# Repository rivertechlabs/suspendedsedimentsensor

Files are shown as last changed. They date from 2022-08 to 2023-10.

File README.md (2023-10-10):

# :ocean:Ötz-T: suspended sediment sensor

## A note on versions:

**This sensor is prototype 3.0 (or "version Ötz-T"). The previous prototype 2.0 (or "first version") is found in this [repo](https://github.com/rivertechlabs/turbiditysensor) (new repo because I consider the two versions different enough).**

## News!

**This sensor was published in HardwareX! Read [Ötz-T: 3D-printed open-source turbidity sensor with Arduino shield for suspended sediment monitoring](https://linkinghub.elsevier.com/retrieve/pii/S2468067223000020).**

-----------------------------------------

**Improvements on this version:**
- :sleeping: Low-power [Arduino MRK WAN 1310](https://store-usa.arduino.cc/products/arduino-mkr-wan-1310) microcontroller
- :stuck_out_tongue_winking_eye: Entirely 3D printed design, so no need to beg a technician for help
- :racehorse: Longer battery life
- :dash: Turbidity, temperature and pressure sensor
- :recycle: Programmed with Arduino IDE
- :dancers: Custom printed circuit board (PCB) as an Arduino shield for an easier and cleaner assembly with a more durable design 

-----------------------------------------
A 3D-printed, open-source suspended sediment sensor for river network monitoring.
## Introduction
This repo is dedicated to the open-source turbidity sensor. More info can be found here:
- https://rivertechlabs.org/
- https://hyd.ifu.ethz.ch/research/riparian/susp-sed-sense.html

This repo contains several items to build the current prototype of the open-source turbidity sensor including:
- The code needed to upload to the microcontroller
- 3D printing files
- PCB files
- CAD files

## Code
There are two codes in the Code folder: main.ino and set_time.ino. Please follow the instructions in set time.ino about changing the date in the program. After the program has flashed, every time the Arduino restarts (disconnect and reconnect to power) it will restart the RTC time to the original compile time of the set time.ino program. To mitigate this issue, the next program, main.ino, can be immediately flashed without disconnecting power or set time.ino can be re-flashed after commenting-out line 79 (“setPCF85263();”). Follow by flashing main.ino onto the Arduino. Please note that additional libraries may need to be downloaded and added to your library (e.g. the [MS5803-05 external library](https://github.com/millerlp/MS5803_05)). The main.ino program was written to take a measurement every hour (one measurement is an average of 15 measurements) to conserve battery, but this can be changed in the code if you require higher temporal resolution to capture larger variability e.g. from flushing of sediment from a dam.

## 3D printing files
Here you will find the printer files (.gcode) and the PrusaSlicer files (.3mf). The CAD files were exported as .stp and imported into the PrusaSlicer program (free). See the .3mf files to understand the settings we used in PrusaSlicer for optimal printing. The main settings were:
- Avoid crossing perimeters [enabled]: so that there was less material to clean after printing
- 5 perimeters, 5 bottom solid layers, and AT LEAST 0.15mm layer height for all components (on the thread and cap to ensure they were waterproof, see this [article](https://blog.prusa3d.com/watertight-3d-printing-pt1-vases-cups-and-other-open-models_48949/))
- The lens inserts ("zapfen") have an even smaller layer height
- The "teeth" have variable layer height (ranging from 0.07-0.15mm to ensure that the zapfen fit into the teeth)

The .3mf files were exported as .gcode files and then printed on a Prusa I3 Mk3 and/or Mk3S Filament Printer.

## PCB
We have provided the Gerber files to directly order the PCBs. Alternatively, the .PcbDoc and .SchDoc files can be opened in Altium (the eductional license can be obtained for free) where you can export your own Gerber files. Finally, the schematic and PCB files were also provided as KiCad files so that they can be viewed and edited without Altium.

## CAD
In this folder we have the original CAD files (as STEP) so that they can be downloaded and adjusted for your project.

## Contact
For questions, please email me at droujko@ifu.baug.ethz.ch or @rivertechjess on Twitter :bird:

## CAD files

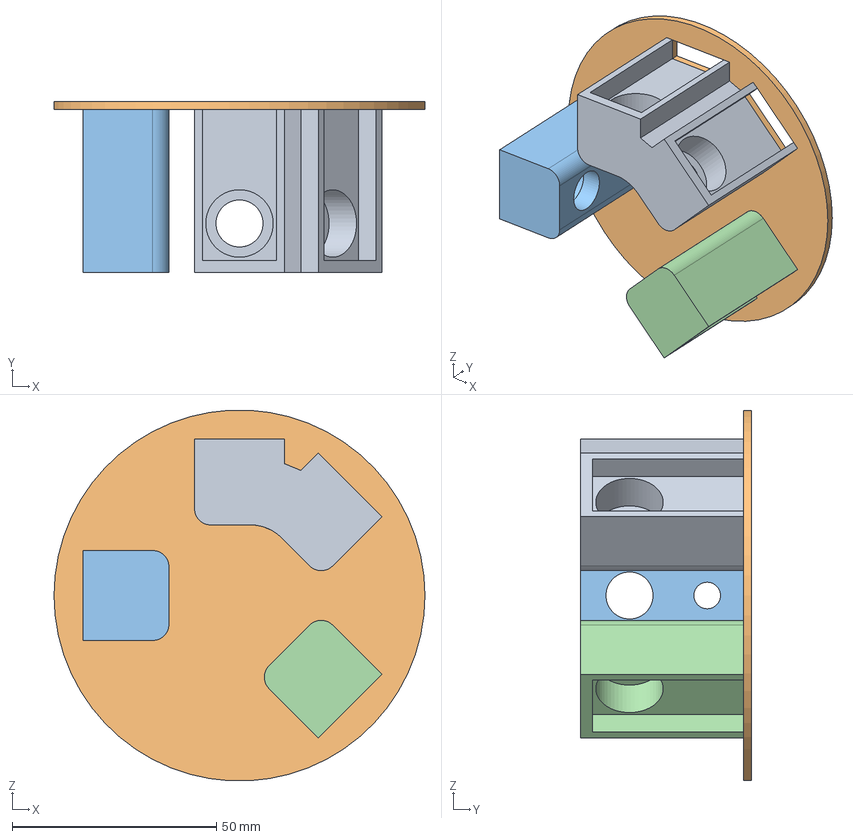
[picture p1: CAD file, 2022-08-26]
CAD/Teeth.step
90.8 x 41.8 x 90.6 mm
Legsandbody (2)
Legsandbody (3)
Legsandbody (1)

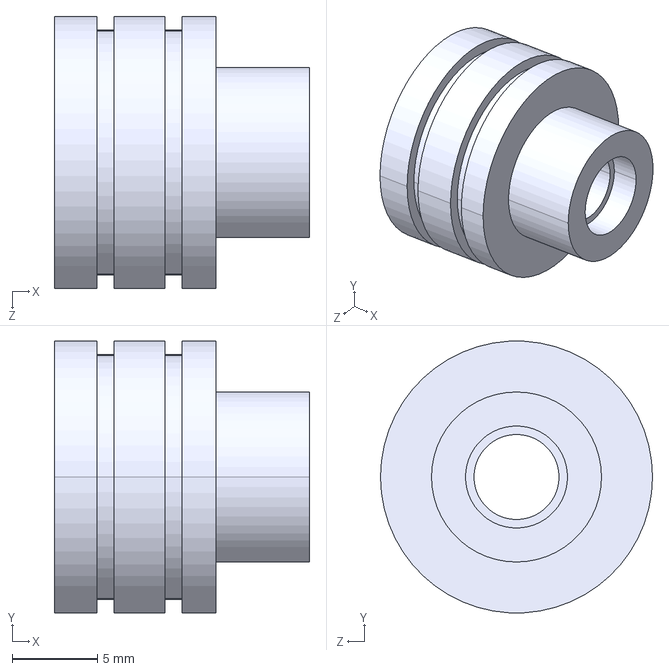
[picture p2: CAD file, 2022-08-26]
CAD/Detector_Zapfen.STEP
15.0 x 16.0 x 16.0 mm

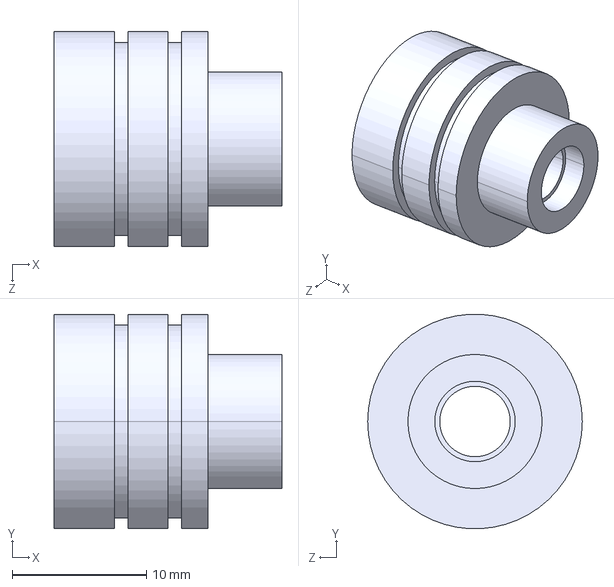
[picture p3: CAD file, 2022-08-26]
CAD/LED_Zapfen.STEP
17.0 x 16.0 x 16.0 mm

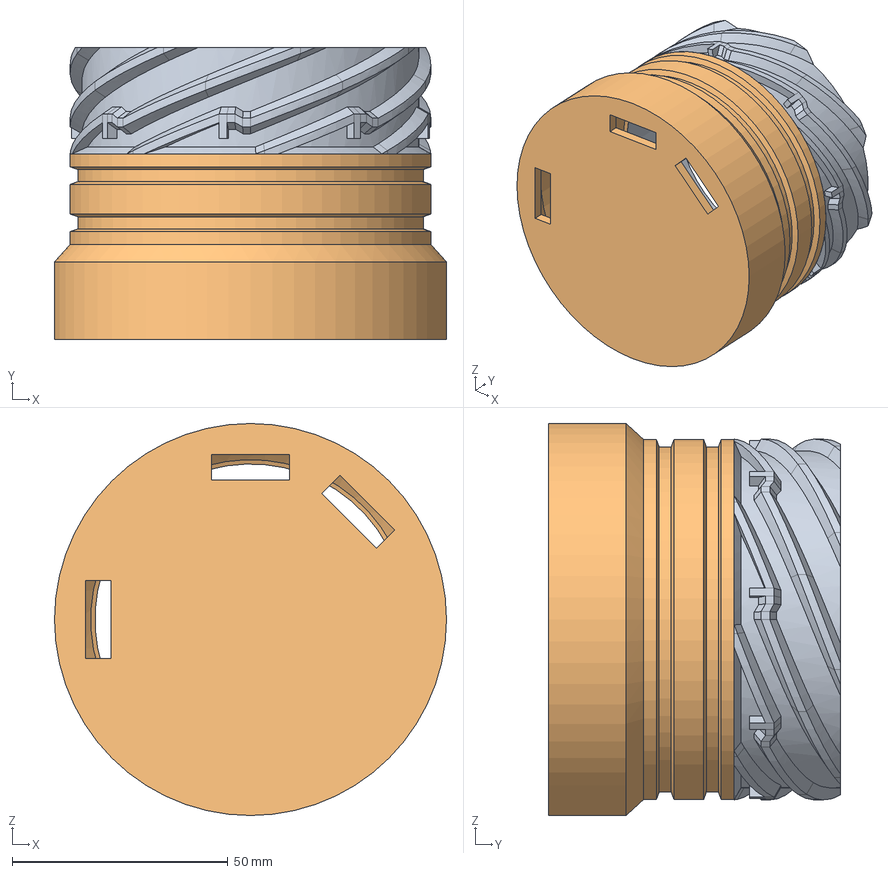
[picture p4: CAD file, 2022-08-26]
CAD/Thread.step
90.8 x 67.6 x 90.8 mm

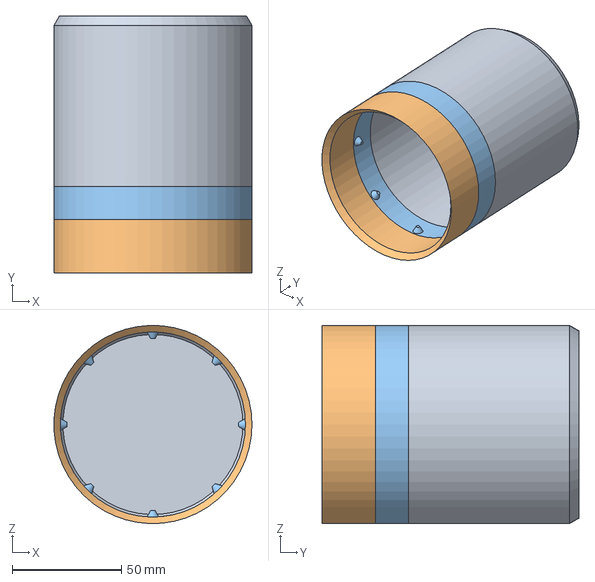
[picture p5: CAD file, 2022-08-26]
CAD/Cap.step
90.7 x 117.5 x 90.7 mm
Cap (1) (1)
Cap

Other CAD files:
3D-printing/Cap.3mf
3D-printing/Cap.stl
3D-printing/Detector_Zapfen.3mf
3D-printing/Detector_Zapfen.STL
3D-printing/LED_Zapfen.3mf
3D-printing/LED_Zapfen.STL
3D-printing/Teeth.3mf
3D-printing/Teeth.stl
3D-printing/Thread.3mf
3D-printing/Thread.stl

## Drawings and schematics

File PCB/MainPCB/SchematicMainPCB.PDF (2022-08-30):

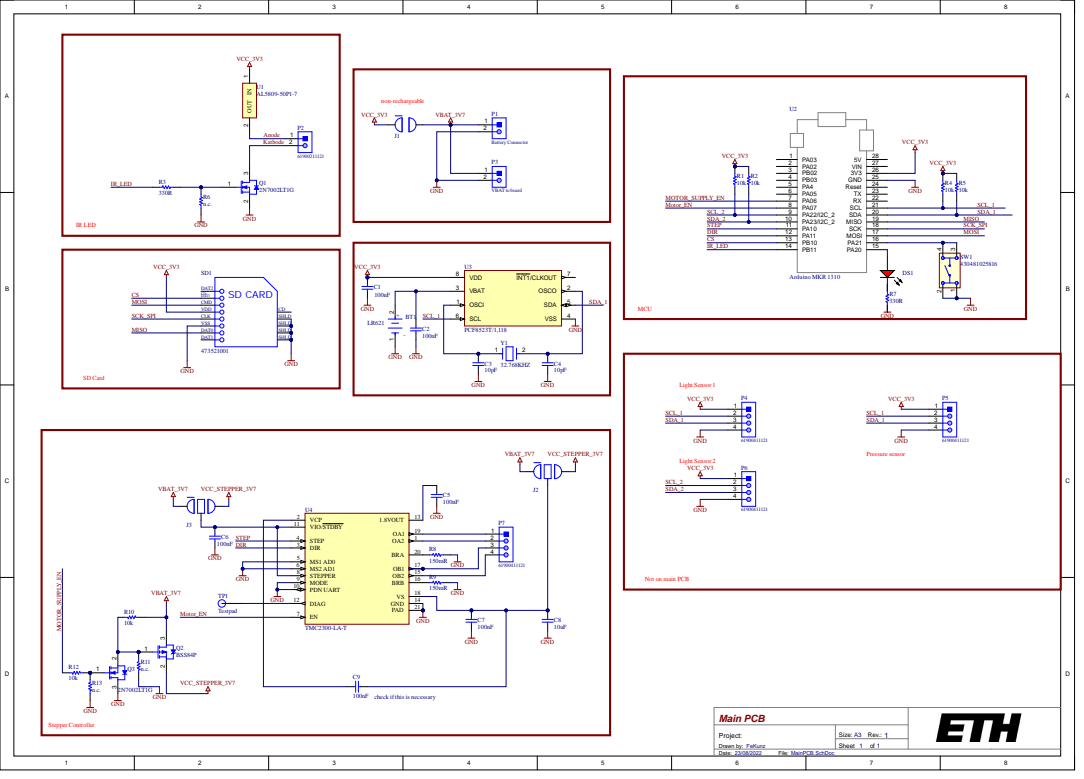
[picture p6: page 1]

1 1 | VCP VIO /ST D B Y ST E P DIR MS1 A D 0 MS2 A D 1 ST EPPE R MO D E PD N U A RT DIA G E N

Main PCB

Pro j e ct : Dra w n by: F eKu n z | Siz e : A3 Rev . : 1

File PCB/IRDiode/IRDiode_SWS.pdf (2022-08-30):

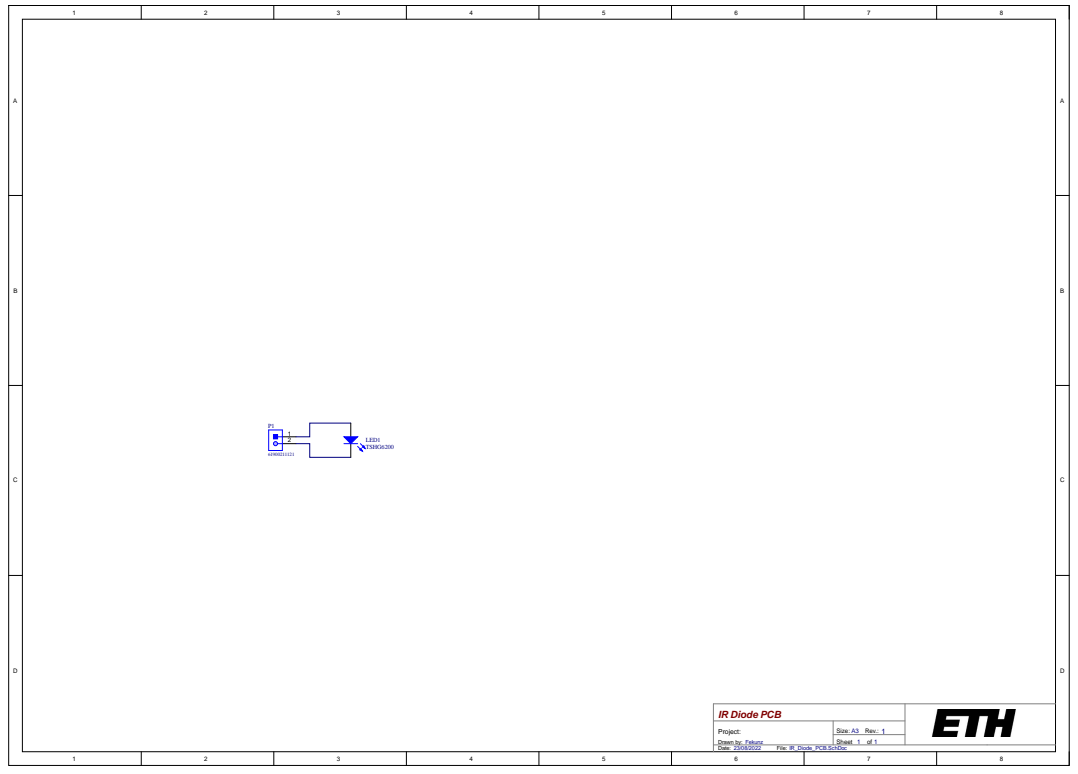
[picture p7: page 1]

IR Dio de PCB

P r oject: Drawn by: Fekun z | S ize: A 3 Rev . : 1

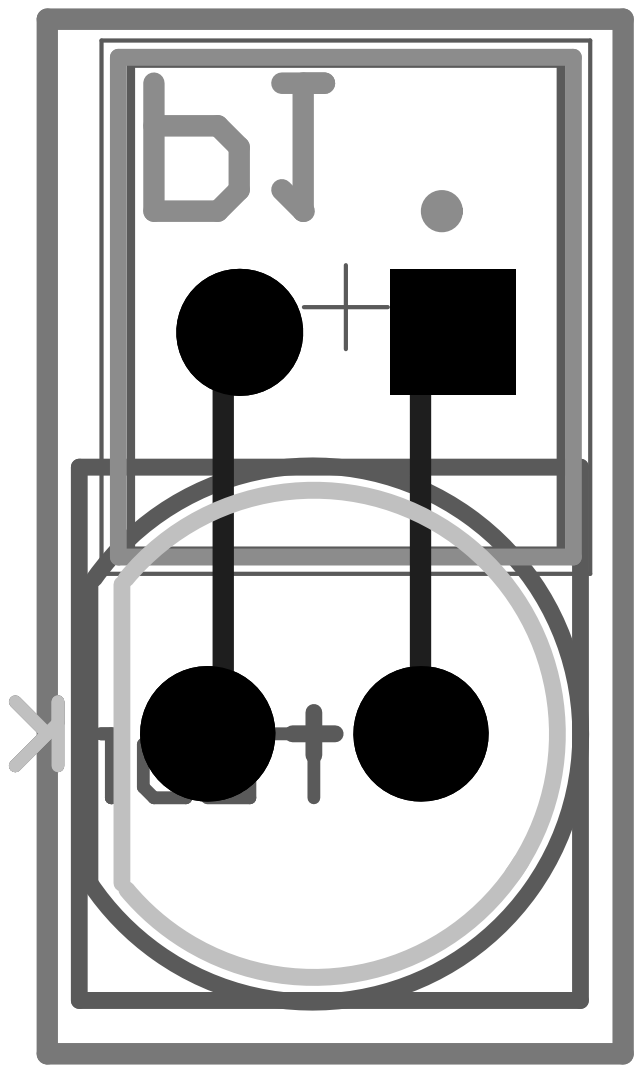
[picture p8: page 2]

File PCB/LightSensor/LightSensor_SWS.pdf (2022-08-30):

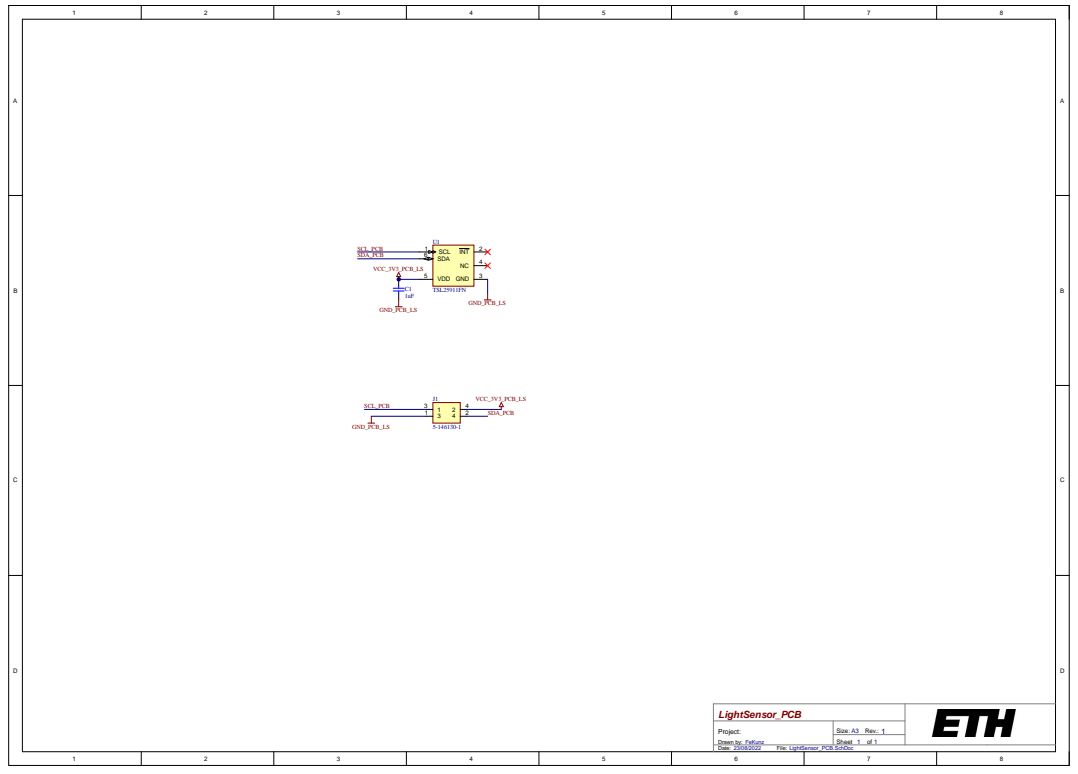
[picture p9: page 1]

LightSensor_PCB

Project: Drawn by: FeKunz | Size: A3 Rev.: 1

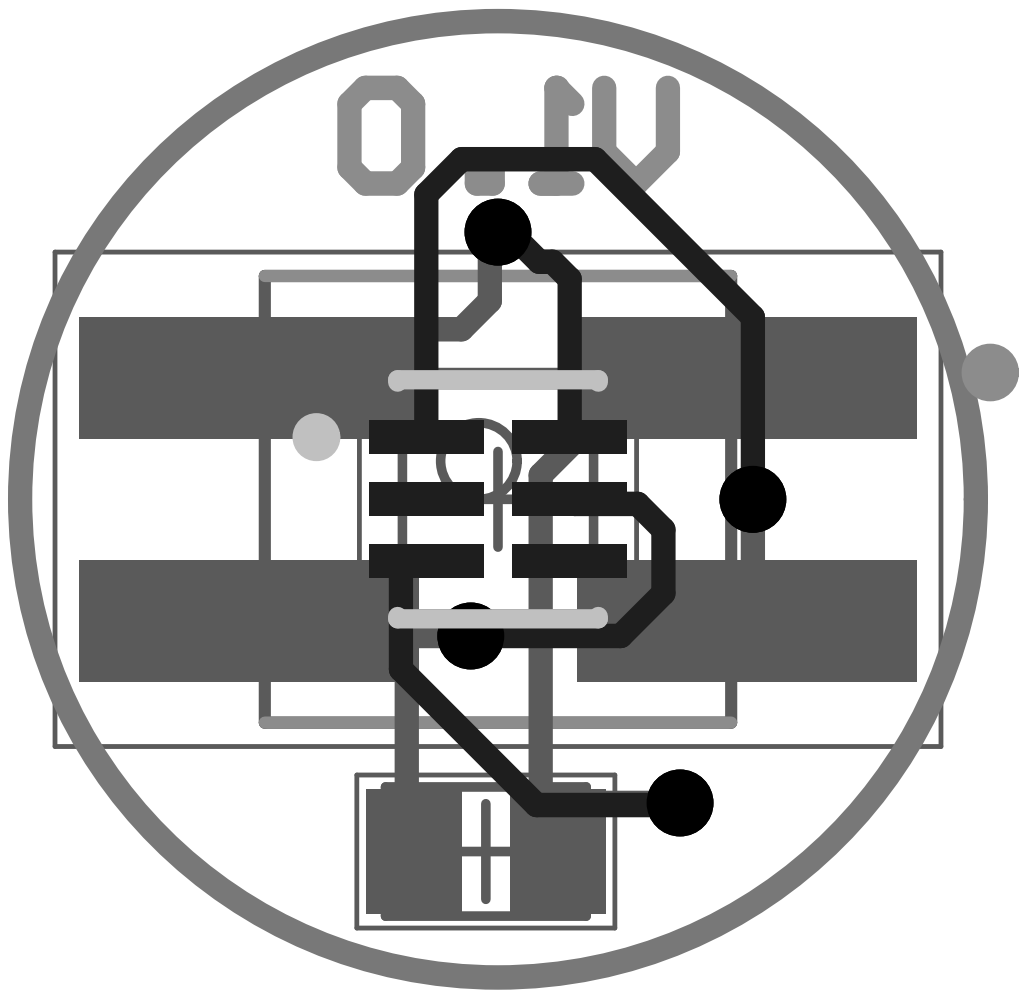
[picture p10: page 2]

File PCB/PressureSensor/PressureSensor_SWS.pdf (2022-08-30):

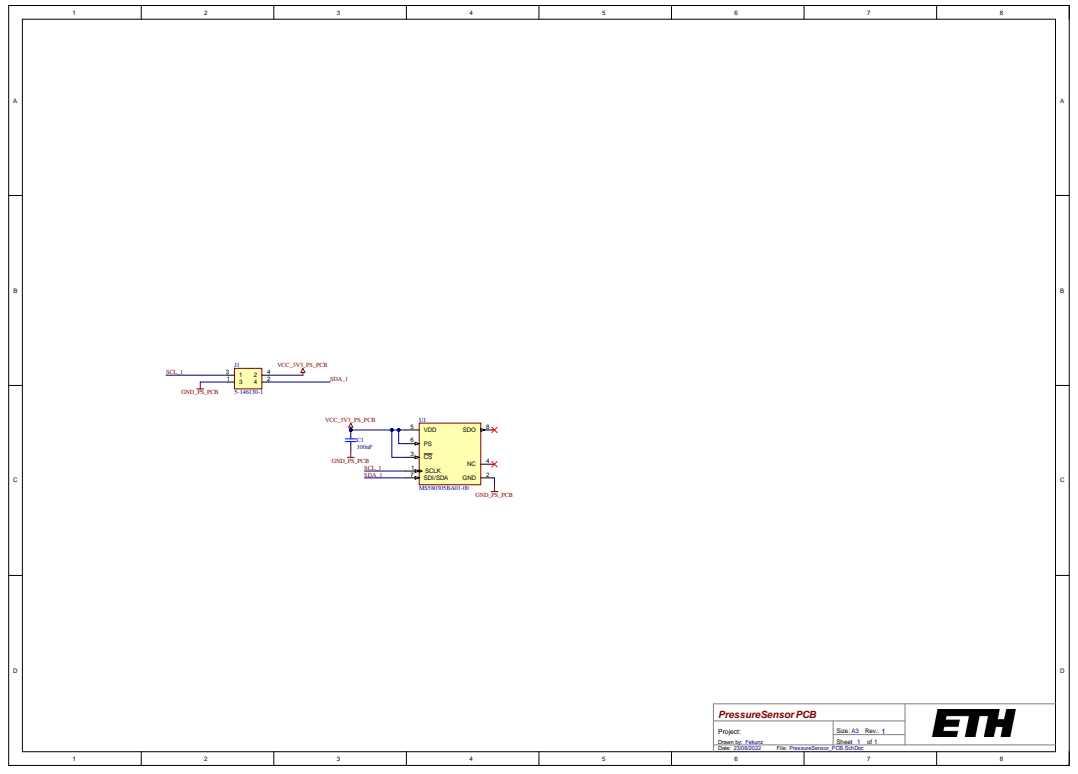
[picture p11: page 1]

Pressu reSenso r P CB

P r oject: Drawn by: Fekun z | S ize: A 3 Rev . : 1

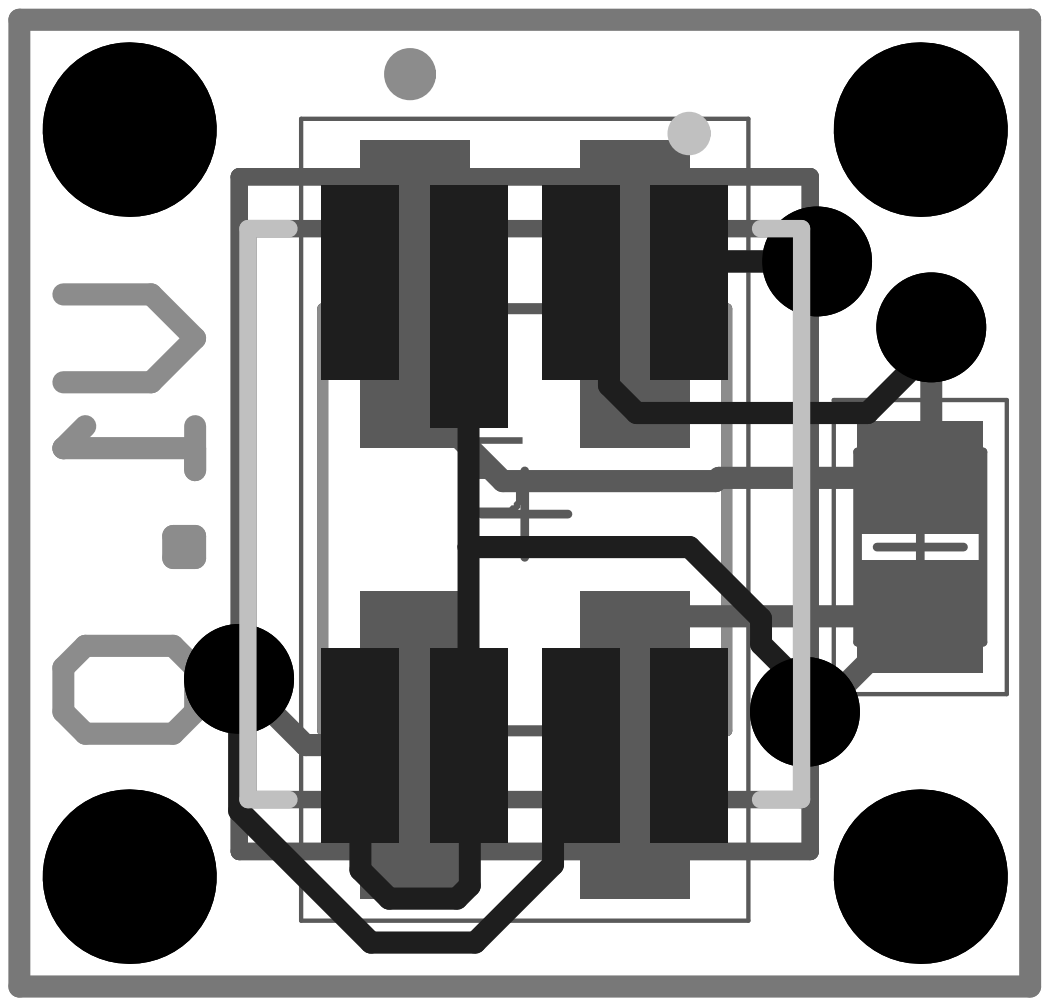
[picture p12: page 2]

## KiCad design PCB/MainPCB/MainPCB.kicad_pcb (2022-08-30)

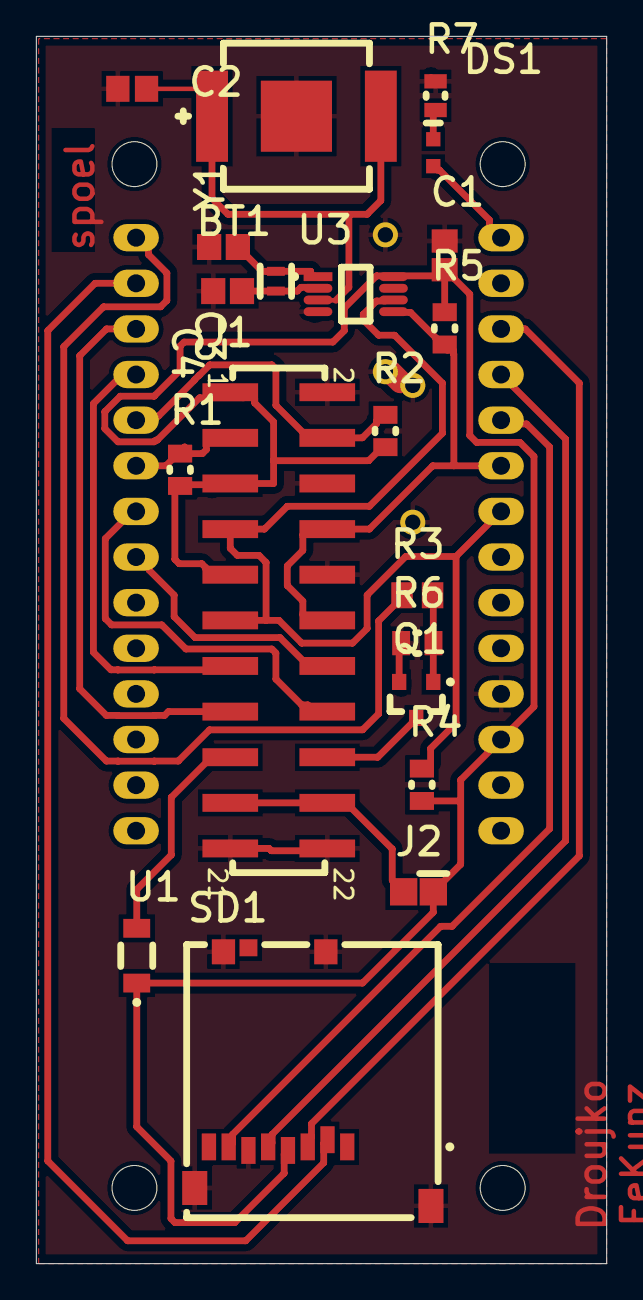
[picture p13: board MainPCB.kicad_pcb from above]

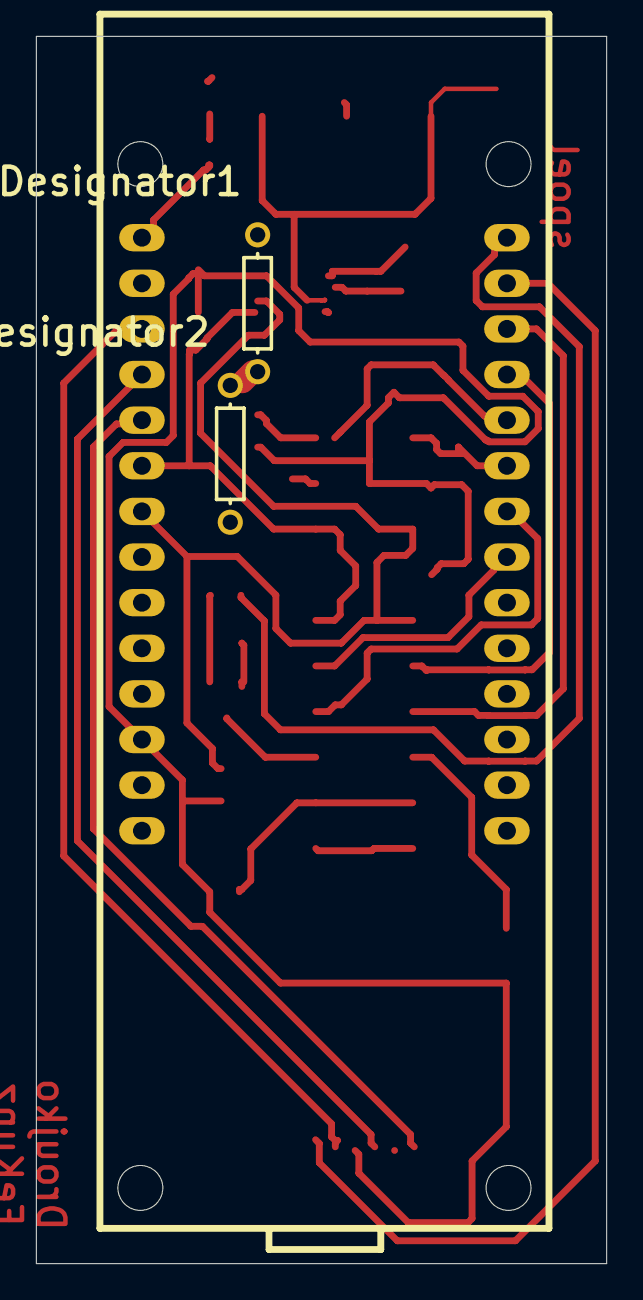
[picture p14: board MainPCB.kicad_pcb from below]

Board: 2 copper layers, 31.7 x 68.3 mm, 23 parts (3 on the bottom side), 24 nets.

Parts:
BT1: LR621; FP-2998-MFG
C1, C2: 100nF; CAPC2013X140X50NL20T25
C3, C4: 10pF; CAPC2013X115X51NL20T26
DS1: HSMH-C190; AVAG-HSMX-C190_V
Designator1, Designator2: Comment; _Users_Public_Documents_Altium_AD21_Library_Miscellaneous D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
J1: 61002221121
J2: Jumper_2W; 2w_Jumper
Q1: 2N7002LT1G; ONSC-SOT-23-3-318-08_V
R1, R2, R4, R5: 10k; RESC2013X60X35NL10T20
R3: 330R; RESC2013X60X40NL20T25
R6: n.c.; RESC2013X60X35NL10T20
R7: 330R; RESC2013X60X35LL10T20
SD1: 473521001; MOLX-473521001_V
U1: AL5809-50P1-7; DIOD-POWERDI123-2_B_V
U2: Arduino MKR 1310; ArduinoMKR
U3: PCF85263ATT/AJ; FP-SOT505-1-IPC_B
Y1: 32.768KHZ; FP-ABS05-MFG

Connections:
Anode: J1.17, U1.2
CS: SD1.2, U2.13
DIR: J1.15, U2.12
GND: BT1.1, C1.1, C2.1, C3.1, C4.1, Designator1.1, Designator1.2, Designator2.1, Designator2.2, J1.2, J1.6, J1.10, J1.21, J1.22, Q1.2, R6.1, R7.2, SD1.6, SD1.10, SD1.11, SD1.12, SD1.13, U2.25, U3.4
IR_LED: R3.1, U2.14
Kathode: J1.18, Q1.3
MISO: SD1.7, U2.19
MOSI: SD1.3, U2.17
MOTOR_SUPPLY_EN: J1.14, U2.7
Motor_EN: J1.16, U2.8
NetBT1_2: BT1.2, C2.2, U3.3
NetC3_2: C3.2, U3.1, Y1.1
NetC4_2: C4.2, U3.2, Y1.2
NetDS1_1: DS1.1, U2.15
NetDS1_2: DS1.2, R7.1
NetQ1_1: Q1.1, R3.2, R6.2
SCK_SPI: SD1.5, U2.18
SCL_1: J1.7, J1.11, R4.1, U2.21, U3.6
SCL_2: J1.3, R1.1, U2.9
SDA_1: J1.8, J1.12, R5.1, U2.20, U3.5
SDA_2: J1.4, R2.1, U2.10
STEP: J1.13, U2.11
VBAT_3V7: J1.19, J1.20, J2.2
VCC_3V3: C1.2, J1.1, J1.5, J1.9, J2.1, R1.2, R2.2, R4.2, R5.2, SD1.4, U1.1, U2.26, U3.8

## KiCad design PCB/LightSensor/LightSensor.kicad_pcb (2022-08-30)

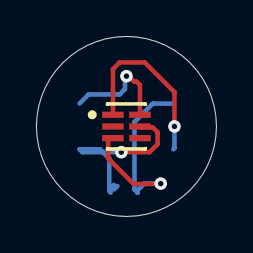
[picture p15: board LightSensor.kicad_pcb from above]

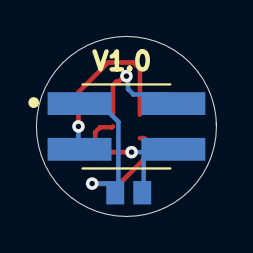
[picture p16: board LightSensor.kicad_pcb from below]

Board: 2 copper layers, 10.0 x 10.0 mm, 3 parts (2 on the bottom side), 4 nets.

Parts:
C1: 1uF; CAPC2013X135X45LL10T25
J1: 5-146130-1; TE_5-146130-1
U1: TSL25911FN; AMS-FN-6-2400X2000DE_V

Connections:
GND_PCB_LS: C1.2, J1.1, U1.3
SCL_PCB: J1.3, U1.1
SDA_PCB: J1.2, U1.6
VCC_3V3_PCB_LS: C1.1, J1.4, U1.5

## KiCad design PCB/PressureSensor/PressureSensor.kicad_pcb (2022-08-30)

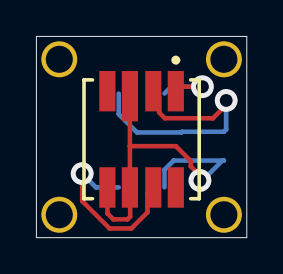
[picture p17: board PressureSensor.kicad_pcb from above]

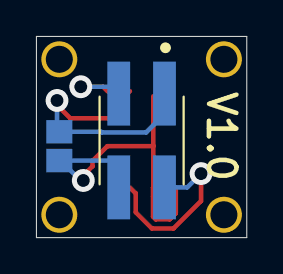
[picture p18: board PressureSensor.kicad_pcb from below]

Board: 2 copper layers, 11.7 x 11.2 mm, 3 parts (2 on the bottom side), 4 nets.

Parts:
C1: 100nF; CAPC2013X140X50NL20T25
J1: 5-146130-1; TE_5-146130-1
U1: MS580305BA01-00; FP-MS580301BA01-00-MFG

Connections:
GND_PS_PCB: C1.1, J1.1, U1.2
SCL_1: J1.3, U1.1
SDA_1: J1.2, U1.7
VCC_3V3_PS_PCB: C1.2, J1.4, U1.3, U1.5, U1.6

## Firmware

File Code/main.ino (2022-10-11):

/******************************************************************************** 
  This code reads turbidity (in Lux) from two light detectors, temperature and pressure
  and saves the data onto an SD card. The code is meant to be loaded onto the Smart Water
  Sensor: Version Rhône. The code enables the sensor to go into extreme low power mode
  (0.07mA during sleep).

  For more information, please visit www.rivertechlabs.org or contact @rivertechjess

******************************************************************************* */

#include "ArduinoLowPower.h"
#include <MKRWAN.h>
#include <Wire.h>
//#include <Arduino_PMIC.h>
#include <Adafruit_Sensor.h>
#include "wiring_private.h"
#include "Adafruit_TSL2591.h"
#include <MS5803_05.h>
#include <SPI.h>
#include <SD.h>
#include <RTCZero.h>

MS_5803 sensor = MS_5803(512);
File myFile; //log file
String filename = "Rhone1.txt"; // name of .txt file with data
int count = 0;
RTCZero rtc;

#define PCF85263address 0x51   //define I2C address 
byte second, minute, hour, dayOfWeek, dayOfMonth, month, year;
String days[] = {"Sunday", "Monday", "Tuesday", "Wednesday", "Thursday", "Friday", "Saturday" };

/******************************************************************************* 
  Define the custom TwoWire instance for SAMD21 since the TSL2591 has one 
  address and we have two TSLs (so we need two I2C busses)
********************************************************************************/
TwoWire myWire(&sercom3, 0, 1);  // Create the new wire instance assigning it to pin 0 and 1
extern "C"{
  void SERCOM3_Handler(void);

  void SERCOM3_Handler(void) {
    myWire.onService();
  }
}

Adafruit_TSL2591 tsl = Adafruit_TSL2591(2591); // pass in a number for the sensor identifier (for your use later)
Adafruit_TSL2591 myTSL = Adafruit_TSL2591(2591); // pass in a number for the sensor identifier (for your use later)

/******************************************************************************* 
  Defining two functions to read the IR value from each TSL sensor on each 
  I2C bus
********************************************************************************/
void readASensor(uint16_t& ir){
  uint32_t lum = tsl.getFullLuminosity();
  ir = lum >> 16;
}

void readBSensor(uint16_t& ir){
  uint32_t lum = myTSL.getFullLuminosity();
  ir = lum >> 16;
}

void readBothChannels(uint16_t& a_ir,uint16_t& b_ir){
  readASensor(a_ir);
  delay(1);
  readBSensor(b_ir);
  delay(1);
}

/******************************************************************************* 
  Function to print time from internal RTC
********************************************************************************/
void print2digits(int number) {
  if (number < 10) {
    Serial.print("0"); // print a 0 before if the number is < than 10
  }
  Serial.print(number);
}

void print2myFile(int number) {
  if (number < 10) {
    myFile.print("0"); // print a 0 before if the number is < than 10
  }
  myFile.print(number);
}

/******************************************************************************* 
  Read date and time from PCF RTC
********************************************************************************/
byte bcdToDec(byte value){
 return ((value / 16) * 10 + value % 16);
}

void readPCF85263() {          // this gets the time and date from the PCF85263
   Wire.beginTransmission(PCF85263address);
   Wire.write(0x01);
   Wire.endTransmission();
   Wire.requestFrom(PCF85263address, 7);
   second     = bcdToDec(Wire.read() & B01111111); // remove VL error bit
   minute     = bcdToDec(Wire.read() & B01111111); // remove unwanted bits from MSB
   hour       = bcdToDec(Wire.read() & B00111111); 
   dayOfMonth = bcdToDec(Wire.read() & B00111111);
   dayOfWeek  = bcdToDec(Wire.read() & B00000111);  
   month      = bcdToDec(Wire.read() & B00011111); // remove century bit, 1999 is over
   year       = bcdToDec(Wire.read());
 }

/******************************************************************************* 
  Print PCF RTC time to serial monitor
********************************************************************************/
void print_PCFtime() {
   Serial.print(days[dayOfWeek]); 
   Serial.print(" ");  
   Serial.print(month, DEC);
   Serial.print("/");
   Serial.print(dayOfMonth, DEC);
   Serial.print("/20");
   Serial.print(year, DEC);
   Serial.print(" - ");
   Serial.print(hour, DEC);
   Serial.print(":");
   if (minute < 10)
 {
   Serial.print("0");
 }
   Serial.print(minute, DEC);
   Serial.print(":");  
   if (second < 10)
 {
   Serial.print("0");
 }  
   Serial.println(second, DEC); 
}

/******************************************************************************* 
  Print MKR RTC time to serial monitor
********************************************************************************/
void print_MKRtime() {
  print2digits(rtc.getDay());
  Serial.print("/");
  print2digits(rtc.getMonth());
  Serial.print("/");
  print2digits(rtc.getYear());
  Serial.print(" ");

  // ...and time
  print2digits(rtc.getHours());
  Serial.print(":");
  print2digits(rtc.getMinutes());
  Serial.print(":");
  print2digits(rtc.getSeconds());

  Serial.println();
}

/******************************************************************************* 
  Write all sensor data to the SD card
********************************************************************************/
void writeToSD(uint16_t& temp, uint16_t& pres, uint16_t& ir_a, uint16_t& ir_b, uint16_t& ir_a_off, uint16_t& ir_b_off){
  if(!myFile)
    return;

   myFile.print(dayOfMonth, DEC);myFile.print("/");
   myFile.print(month, DEC);myFile.print("/20");myFile.print(year, DEC);
   myFile.print(" ");
   myFile.print(hour, DEC);myFile.print(":");
   if (minute < 10){
      myFile.print("0");
    }
   myFile.print(minute, DEC);myFile.print(":");  
   if (second < 10){
      myFile.print("0");
    }  
   myFile.print(second, DEC); myFile.print(", ");

  print2myFile(rtc.getDay());myFile.print("/");
  print2myFile(rtc.getMonth());myFile.print("/");
  print2myFile(rtc.getYear());
  myFile.print(" ");
  print2myFile(rtc.getHours());myFile.print(":");
  print2myFile(rtc.getMinutes());myFile.print(":");
  print2myFile(rtc.getSeconds()); myFile.print(", ");

  myFile.print(temp); myFile.print(", ");
  myFile.print(pres); myFile.print(", ");
  myFile.print(ir_a); myFile.print(", ");
  myFile.print(ir_b); myFile.print(", ");
  myFile.print(ir_a_off); myFile.print(", ");
  myFile.println(ir_b_off);
  
}

/******************************************************************************* 
  Set up the code; to be run upon reset or initialization
********************************************************************************/
void setup() {
  Serial.begin(9600);

  //----------- Initialize internal RTC sensor
  rtc.begin(); // initialize RTC

  rtc.setTime(0, 0, 0);
  rtc.setDate(1, 1, 00);

  //----------- Initialize the IR sensor
  if (tsl.begin()) {
    Serial.println(F("Found a TSL2591 sensor"));
  } else {
    Serial.println(F("No sensor found ... check your wiring?"));
  }

  //----------- Initialize the MS5803 sensor
  if (sensor.initializeMS_5803(false)) { // used "false" here so all coefs. aren't printed
    Serial.println( "MS5803 CRC check OK." );
  } else {
    Serial.println( "MS5803 CRC check FAILED!" );
  }

  //----------- Initialize the second I2C channels
  pinPeripheral(0, PIO_SERCOM);  // PAD[0]   //Assign SDA function to pin 0
  pinPeripheral(1, PIO_SERCOM);  // PAD[1]   //Assign SCL function to pin 1

  if (myTSL.begin(&myWire)){
    Serial.println(F("Found a TSL2591 sensor"));
  } else {
    Serial.println(F("No sensor found ... check your wiring?"));
  }

  //----------- Initialize the SD card
  Serial.print("Initializing SD card...");
  if (!SD.begin(4)) { // initialize
    Serial.println("initialization failed!");
  }
  Serial.println("initialization done.");

  //----------- Set up and write first line to .csv file
  myFile = SD.open(filename, FILE_WRITE);
  if (myFile) {
    Serial.println("test.txt - Created");
    Serial.print("Writing to test.txt...");
    myFile.println("DateTimePCF, DateTimeMKR, Temperature, Pressure, IR_A, IR_B, IR_A_OFF, IR_B_OFF");
    Serial.println("done.");
    myFile.close();
  } else {
    Serial.println("error opening test.txt");
  }

  //----------- Initialize LED
  pinMode(5, OUTPUT);
  digitalWrite(5, LOW);
  
  //----------- Set all other pins to INPUT_PULLUP so lowest current draw in sleep
  pinMode(LED_BUILTIN, OUTPUT);
  //pinMode(0, INPUT_PULLUP); //SDA2
  //pinMode(1, INPUT_PULLUP); //SCL2
  pinMode(2, INPUT_PULLUP); //motor step
  pinMode(3, INPUT_PULLUP); //motor dir
  //pinMode(4, INPUT_PULLUP); //CS of SD card
  //pinMode(5, INPUT_PULLUP); // IR LED
  //pinMode(6, INPUT_PULLUP); //isRecording LED (also connected to on board LED)
  pinMode(7, INPUT_PULLUP); //isRecording switch
  /*pinMode(8, INPUT_PULLUP); // next three are for SD card
  pinMode(9, INPUT_PULLUP);
  pinMode(10, INPUT_PULLUP);
  pinMode(11, INPUT_PULLUP); // next two are SDA1 and SCL1
  pinMode(12, INPUT_PULLUP);*/
  pinMode(13, INPUT_PULLUP);
  pinMode(14, INPUT_PULLUP);
}

void loop() {
  
  uint16_t degree, pascals, high_300_full_a, high_300_ir_a, high_300_full_b, high_300_ir_b;
  uint16_t high_300_full_a_avg, high_300_ir_a_avg, high_300_full_b_avg, high_300_ir_b_avg;
  uint16_t high_300_full_a_avg_off, high_300_ir_a_avg_off, high_300_full_b_avg_off, high_300_ir_b_avg_off;

  readPCF85263();
  Serial.print("PCF time: ");
  print_PCFtime();
  Serial.print("MKR time: ");
  print_MKRtime();
  
  sensor.readSensor(); // get pressure and temperature reading. 

  pascals = sensor.pressure();
  Serial.print("Pressure = ");
  Serial.print(pascals);
  Serial.println(" mbar");
  
  degree = sensor.temperature();
  Serial.print("Temperature = ");
  Serial.print(degree);
  Serial.println("C");

  // set gain and integration time for IR detectors
  myTSL.setGain(TSL2591_GAIN_HIGH);
  myTSL.setTiming(TSL2591_INTEGRATIONTIME_300MS);

  tsl.setGain(TSL2591_GAIN_HIGH);
  tsl.setTiming(TSL2591_INTEGRATIONTIME_300MS);

  // turn on LED
  digitalWrite(5, HIGH);
  delay(100); //allow LED to heat up

  int sen = 1;
  long high_300_ir_a_tot = 0;
  long high_300_ir_b_tot = 0;
      
  while (sen < 16){ //average of 15 measurements
    readBothChannels(high_300_ir_a, high_300_ir_b);
    high_300_ir_a_tot = high_300_ir_a_tot + high_300_ir_a;
    high_300_ir_b_tot = high_300_ir_b_tot + high_300_ir_b;
    sen = sen + 1;
  }

  high_300_ir_a_avg = high_300_ir_a_tot / 15;
  high_300_ir_b_avg = high_300_ir_b_tot / 15;

  // turn off LED
  digitalWrite(5, LOW);

  int sen_off = 1;
  high_300_ir_a_tot = 0;
  high_300_ir_b_tot = 0;
      
  while (sen_off < 3){
    readBothChannels(high_300_ir_a, high_300_ir_b);
    high_300_ir_a_tot = high_300_ir_a_tot + high_300_ir_a;
    high_300_ir_b_tot = high_300_ir_b_tot + high_300_ir_b;
    sen_off = sen_off + 1;
  }

  high_300_ir_a_avg_off = high_300_ir_a_tot / 2;
  high_300_ir_b_avg_off = high_300_ir_b_tot / 2;
  
  Serial.print(high_300_ir_a_avg_off);Serial.print(",");
  Serial.print(high_300_ir_b_avg_off);Serial.print(",");
  
  Serial.print(high_300_ir_a_avg);Serial.print(",");
  Serial.println(high_300_ir_b_avg);

  myFile = SD.open(filename, FILE_WRITE);
  if (myFile) {
    Serial.println("File opened");
  }

  writeToSD(degree,pascals,high_300_ir_a_avg, high_300_ir_b_avg, high_300_ir_a_avg_off, high_300_ir_b_avg_off);

  tsl.disable();
  
  myFile.close();
  Serial.println("File closed");
  Serial.println("");

  LowPower.deepSleep(3600000);
  // sensor enters deep sleep for 1h: 3 600 000  = 60min*60sec*1000mili
}
